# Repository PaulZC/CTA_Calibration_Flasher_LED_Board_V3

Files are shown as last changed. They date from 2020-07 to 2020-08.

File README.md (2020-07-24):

# CTA Calibration Flasher: LED Board V3

A nanosecond LED flasher board which provides digital control of both pulse width and LED current. Designed to aid
photomultiplier detector calibration and characterisation.

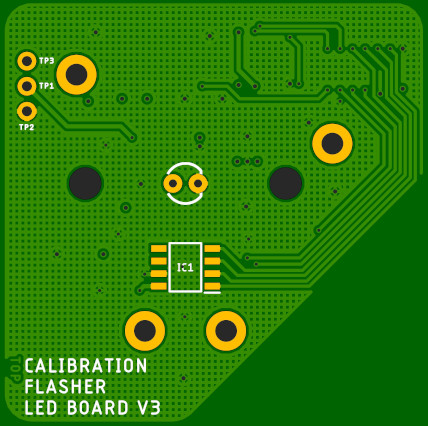
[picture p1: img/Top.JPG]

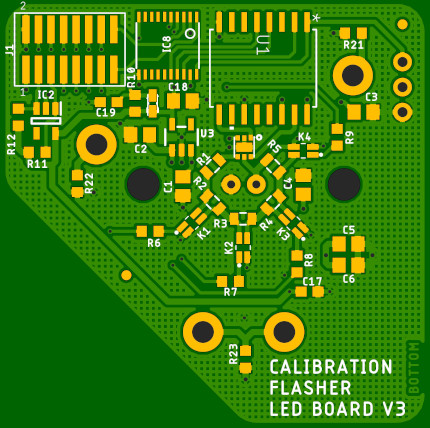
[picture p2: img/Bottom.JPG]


The design of this board is based extensively on that of the [Nanosecond LED Flasher Shield](https://github.com/PaulZC/Nanosecond_LED_Flasher_Shield).

The LED is driven by the [LMG1025 from Texas Instruments](http://www.ti.com/product/LMG1025-Q1).
Designed for automotive LIDAR applications, this gate driver has typical rise and fall times of 650ps
and 850ps and can produce 5V pulse widths as short as 1.25ns.

The pulse width is controlled by a [Maxim Integrated DS1023S-25+](https://www.maximintegrated.com/en/products/analog/clock-generation-distribution/DS1023.html)
programmable timing element which can produce digitally-adjustable pulse widths of 0 to ~64ns in 0.25ns increments.

The LED current is set by five surface mount resistors connected in series, four of which can be shorted
out by [Toshiba TLP3475 photorelays](https://toshiba.semicon-storage.com/ap-en/semiconductor/product/optoelectronics/photorelay-mosfet-output/detail.TLP3475.html)
allowing the LED current to be adjusted digitally in 16 increments.

The board is designed to be mounted on and controlled by the [CTA Calibration Flasher Controller Board V3](https://github.com/PaulZC/CTA_Calibration_Flasher_Controller_Board_V3).

The temperature can be measured via an [ADT7310 16-bit SPI temperature sensor](https://www.analog.com/en/products/adt7310.html).

The board is also equipped with a [DS28CM00 I<sup>2</sup>C silicon serial number](https://www.maximintegrated.com/en/products/ibutton-one-wire/memory-products/DS28CM00.html)
to allow the board to be uniquely identified during calibration.

To aid the mounting of a diffuser or fibre-coupling optics, a modified [ThorLabs S1LEDM SM1 threaded mount](https://www.thorlabs.de/thorproduct.cfm?partnumber=S1LEDM)
can be mounted onto the circuit board.

Please note that this board requires 5V power but that all I/O signals are 3.3V.

## Repository Contents

- **/Documentation** - Documentation for the hardware
- **/Hardware** - BOM, schematic, Eagle PCB design files and Gerber files
- **LICENSE.md** contains the licence information

## Documentation

- [Hardware overview](./Documentation/README.md): an overview of the hardware

Enjoy!

**_Paul_**

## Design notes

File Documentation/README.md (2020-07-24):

# CTA Calibration Flasher: LED Board V3: Hardware Overview

A nanosecond LED flasher board which provides digital control of both pulse width and LED current. Designed to aid
photomultiplier detector calibration and characterisation.

Top

Bottom

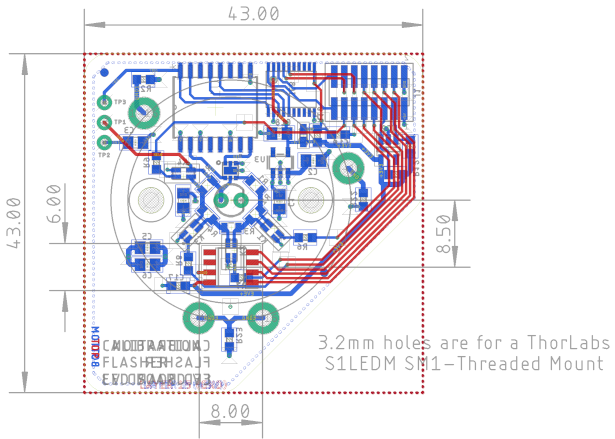
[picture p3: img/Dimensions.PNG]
Dimensions


The full schematic is available [here](../Hardware/Flasher_LED_Board_V3.pdf).

## LMG1025

The LED is driven by the new [LMG1025 from Texas Instruments](http://www.ti.com/product/LMG1025-Q1).
Designed for automotive LIDAR applications, this gate driver has typical rise and fall times of 650ps
and 850ps and can produce 5V pulse widths as short as 1.25ns.

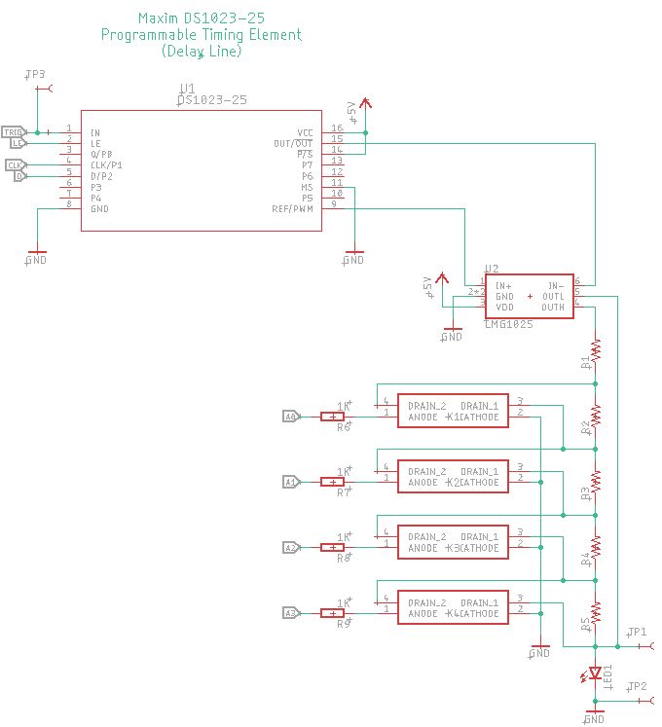
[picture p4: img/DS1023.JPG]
DS1023


The functional block diagram for the LMG1025 is:

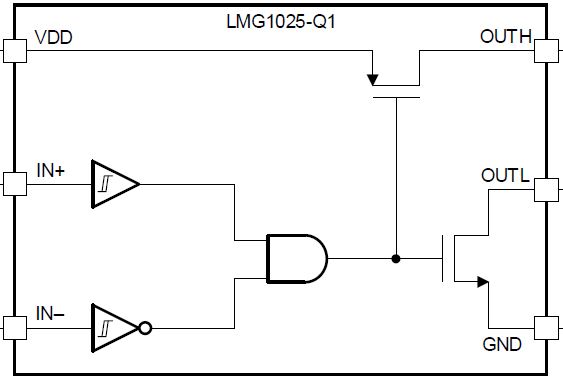
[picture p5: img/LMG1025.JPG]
LMG1025


The LMG1025 is designed to drive a GaN FET to switch a LIDAR source, but with pull-up and pull-down
current limits of 7A and 5A it can of course drive a standard or high-brightness LED directly.

The truth table for the LMG1025 is:

Truth Table

It is important to note that OUTH is pulled up to 5V only when IN+ is high and IN- is low. In each of the other
three possible states, OUTL is pulled low. We can take advantage of this by connecting OUTH to the current-limiting
resistor and OUTL directly to the LED anode. This allows the LED to be turned off very quickly.

## DS1023

The Maxim Integrated DS1023S-25+ is a programmable timing element with two outputs: OUT and REF. The delay between IN and
OUT is digitally-programmable from 0ns to ~64ns in 256 0.25ns increments. There is also an additional inherent "step zero"
delay between IN and OUT caused by the propagation delay through the chip. The REF output is delayed by a small fixed delay
of approximately 1.5ns plus the same "step zero" delay. By driving the LMG1025 IN+ and IN- from REF and OUT respectively,
the LED pulse can be adjusted from essentially zero pulse width (+/-0.125ns) to a maximum of 62.5ns (64ns - 1.5ns).
The LED turns on when REF goes high, and off again when OUT goes high.

## Photorelays

Five resistors, connected in series, are connected between the LMG1025 OUTH pin and the LED anode. By shorting out four
of these resistors in 16 permutations, the LED current can be adjusted between minimum and maximum values dictated by
the selection of resistor values. The resistors are shorted out by TLP3475 photorelays which provide fast response times
and an on-resistance of approximately 1ohm.

For example: with resistances of 10, 18, 22, 27 and 33 ohms, with the 10 ohm resistor always in circuit, it is possible to achieve
an even spread of resistance values from 13.8 ohms to 110 ohms.

## ADT7310

The temperature can be measured via an [ADT7310 16-bit SPI temperature sensor](https://www.analog.com/en/products/adt7310.html).

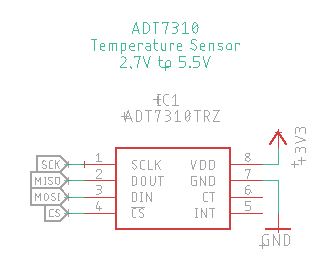
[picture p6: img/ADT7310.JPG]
ADT7310


## DS28CM00

The board is also equipped with a [DS28CM00 I<sup>2</sup>C silicon serial number](https://www.maximintegrated.com/en/products/ibutton-one-wire/memory-products/DS28CM00.html)
to allow the board to be uniquely identified during calibration.

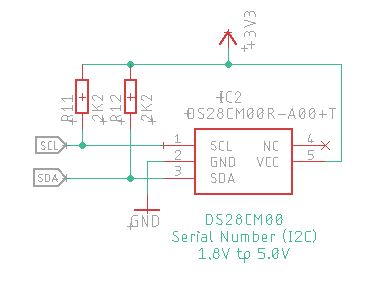
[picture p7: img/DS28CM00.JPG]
DS28CM00


## Connector

The connector is a [Samtec FW-08-05](https://www.samtec.com/products/fw-sm)

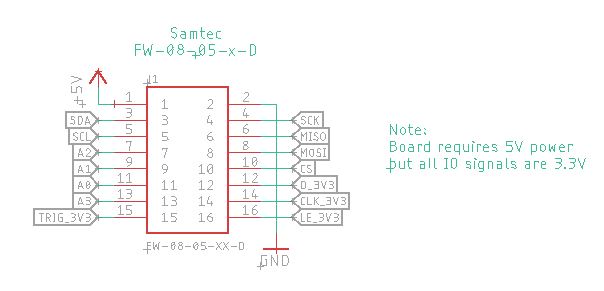
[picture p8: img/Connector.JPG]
Connector


The pin allocation is:
- 1: +5V power
- 2: GND (0V)
- 3: I<sup>2</sup>C SDA (DS28CM00)
- 4: SPI SCK (ADT7310)
- 5: I<sup>2</sup>C SCL (DS28CM00)
- 6: SPI CIPO (ADT7310)
- 7: Photorelay A2
- 8: SPI COPI (ADT7310)
- 9: Photorelay A1
- 10: SPI CS (ADT7310)
- 11: Photorelay A0
- 12: DS1023 Data
- 13: Photorelay A3
- 14: DS1023 CLK
- 15: Trigger signal
- 16: DS1023 Latch Enable

## TXB0108

To minimise congestion on the matching controller board, all I/O signals from the controller board to the LED board are 3.3V.
However, the DS1023 is of course a 5V device. A [TXB0108](https://www.ti.com/product/TXB0108) 8-bit bidirectional voltage-level shifter
converts the 3.3V signals to 5V.

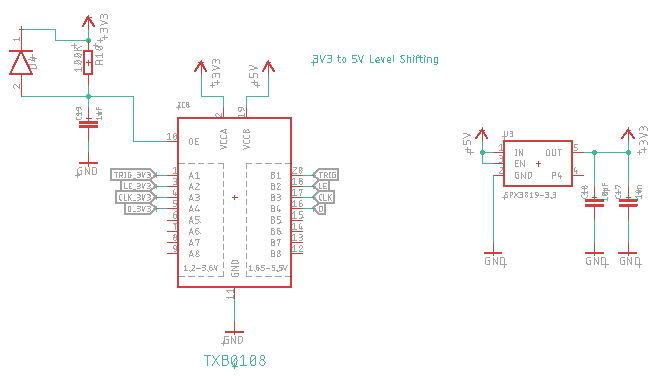
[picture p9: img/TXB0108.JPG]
TXB0108


## ThorLabs S1LEDM SM1

To aid the mounting of a diffuser or fibre-coupling optics, a modified [ThorLabs S1LEDM SM1 threaded mount](https://www.thorlabs.de/thorproduct.cfm?partnumber=S1LEDM)
can be mounted onto the circuit board.

It is necessary to:
- drill and tap the two spanner wrench slots to M3.0
  - the wrench slots are separated by 20.32mm in X
- mill a recess/pocket for the ADT7310
  - the pocket needs to be:
    - 8mm x 6mm
    - with a corner (tool) radius of 1mm
    - offset by 8.50mm in Y from the center of the part

Dimensions

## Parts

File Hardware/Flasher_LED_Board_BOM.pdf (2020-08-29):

Part | X | | Y | Angle | Package | Value | Manufacturer | Manufacturer Part No | Mouser Part No | Descripon
Dimensions 43.00 | 43.00

Fiducials - for solder paste mask alignment:

FD1 | 2.54 | 40.46 | 40.64 | 0 | | | | | | Fiducial 1mm
FD2 | 30.48 | 12.52 | 15.24 | 0 | | | | | | Fiducial 1mm

Surface Mount Components (Top):

IC1 | 18.62 | 16.94 | 180 | 8-Lead SOIC_N (R-8) ADT7310TRZ | Analog Devices | ADT7310TRZ | 2067805 584-ADT7310TRZ-R7 | Temperature Sensor IC, Digital, ± 0.5°C, -55 °C, +150 °C

Surface Mount Components (Boom):

C1 | 24.77 | 18.23 | 24.26 | 270 | 0805 | 10nF | Walsin | 0805B103K500CT | 2496939 | MulLayer Ceramic Capacitor; 10nF; 50V; 0805; X7R
C2 | 29.08 | 13.92 | 29.46 | 180 | 0805 | 10uF | Walsin | 0805F106Z100CT | 2496998 | MulLayer Ceramic Capacitor; 10uF; 10V; 0805
C3 | 6.48 | 36.52 | 31.75 | 0 | 0805 | 10nF | Walsin | 0805B103K500CT | 2496939 | MulLayer Ceramic Capacitor; 10nF; 50V; 0805; X7R
C4 | 12.57 | 30.43 | 24.38 | 90 | 0805 | 10uF | Walsin | 0805F106Z100CT | 2496998 | MulLayer Ceramic Capacitor; 10uF; 10V; 0805
C5 | 8 | 35.00 | 18.41 | 0 | 0805 | 10nF | Walsin | 0805B103K500CT | 2496939 | MulLayer Ceramic Capacitor; 10nF; 50V; 0805; X7R
C6 | 8 | 35.00 | 16.26 | 0 | 0805 | 10uF | Walsin | 0805F106Z100CT | 2496998 | MulLayer Ceramic Capacitor; 10uF; 10V; 0805
C17 | 11.94 | 31.06 | 13.59 | 0 | 0603 | 10nF | Walsin | 0201B103K100CT | 2496756 | MulLayer Ceramic Capacitor; 10nF; 10V; 0603; X7R
C18 | 24.77 | 18.23 | 32.89 | 0 | 0805 | 10uF | Walsin | 0805F106Z100CT | 2496998 | MulLayer Ceramic Capacitor; 10uF; 10V; 0805
C19 | 32.26 | 10.74 | 32.77 | 180 | 0603 | 1uF | Walsin | 0603X105K100CT | 2496916 | MulLayer Ceramic Capacitor; 1uF; 10V; 0603; X5R
D4 | 27.81 | 15.19 | 32.64 | 90 | 0603 | CD0603-B00340 | Bourns | CD0603-B00340 | 1456534 | Small Signal Schoky Diode, 40 V, 370 mV, 500 mA
IC2 | 38.61 | 4.39 | 30.86 | 270 | SOT23-5 | DS28CM00R-A00+T | Maxim | DS28CM00R-A00+T | 2514574 700-DS28CM00R-A00T | Maxim (Dallas Semi) I2C/SMBus Silicon Serial Number
IC8 | 26.29 | 16.71 | 38.48 | 180 | TSSOP20 | TXB0108PWR | Texas Inst. | TXB0108PWR | 1494945 | Voltage Level Translator; 8 Input; TSSOP-20
J1 | 36.2 | 6.80 | 38.1 | 0 | | | Samtec
K1 | 23.85 | 19.15 | 20.55 | 315 | | | Toshiba | TLP3475RTPF | 757-TLP3475TPF | Toshiba TLP3475 Photorelay (not TLP3475R)
K2 | 18.65 | 24.35 | 18.03 | 0 | | | Toshiba | TLP3475RTPF | 757-TLP3475TPF | Toshiba TLP3475 Photorelay (not TLP3475R)
K3 | 13.56 | 29.44 | 20.48 | 45 | | | Toshiba | TLP3475RTPF | 757-TLP3475TPF | Toshiba TLP3475 Photorelay (not TLP3475R)
K4 | 12.57 | 30.43 | 27.83 | 90 | | | Toshiba | TLP3475RTPF | 757-TLP3475TPF | Toshiba TLP3475 Photorelay (not TLP3475R)
R1 | 21.72 | 21.28 | 26.29 | 45 | 0805 | | | | | Select on test: suggested value 10R
R2 | 21.72 | 21.28 | 22.61 | 135 | 0805 | | | | | Select on test: suggested value 18R
R3 | 18.67 | 24.33 | 20.96 | 180 | 0805 | | | | | Select on test: suggested value 22R
R4 | 15.62 | 27.38 | 22.61 | 225 | 0805 | | | | | Select on test: suggested value 27R
R5 | 15.62 | 27.38 | 26.29 | 315 | 0805 | | | | | Select on test: suggested value 33R
R6 | 28.07 | 14.93 | 19.69 | 180 | 0603 | 1K | Mulcomp | MCWR06X1001FTL | 2447272 | Chip Resistor; Thick Film; 1k; 50V; 0603; 100mW
R7 | 19.94 | 23.06 | 14.61 | 180 | 0603 | 1K | Mulcomp | MCWR06X1001FTL | 2447272 | Chip Resistor; Thick Film; 1k; 50V; 0603; 100mW
R8 | 13.21 | 29.79 | 16.38 | 270 | 0603 | 1K | Mulcomp | MCWR06X1001FTL | 2447272 | Chip Resistor; Thick Film; 1k; 50V; 0603; 100mW
R9 | 9.14 | 33.86 | 29.21 | 90 | 0603 | 1K | Mulcomp | MCWR06X1001FTL | 2447272 | Chip Resistor; Thick Film; 1k; 50V; 0603; 100mW
R10 | 29.59 | 13.41 | 32.64 | 90 | 0603 | 100K | Mulcomp | MCWR06X1002FTL | 2447230 | Chip Resistor; Thick Film; 10k; 50V; 0603; 100mW
R11 | 39.5 | 3.50 | 27.69 | 180 | 0603 | 2K2 | Mulcomp | MCWR06X2201FTL | 2447320 | Chip Resistor; Thick Film; 2.2k; 50V; 0603; 100mW
R12 | 41.4 | 1.60 | 31.24 | 270 | 0603 | 2K2 | Mulcomp | MCWR06X2201FTL | 2447320 | Chip Resistor; Thick Film; 2.2k; 50V; 0603; 100mW
R21 | 7.49 | 35.51 | 39.75 | 180 | 0603 | 0R | Mulcomp | MCMR06X000PTL | 2073345 | SMD Chip Resistor, 0 ohm, 75 V, 0603, 100 mW
R22 | 35.43 | 7.57 | 24.51 | 270 | 0603 | 0R | Mulcomp | MCMR06X000PTL | 2073345 | SMD Chip Resistor, 0 ohm, 75 V, 0603, 100 mW
R23 | 18.41 | 24.59 | 6.73 | 270 | 0603 | 0R | Mulcomp | MCMR06X000PTL | 2073345 | SMD Chip Resistor, 0 ohm, 75 V, 0603, 100 mW
U1 | 16.64 | 26.36 | 36.2 | 270 | WSOIC-16 | DS1023-25 | Maxim | DS1023S-25+ | 2516605 700-DS1023S-25 | Delay Line; 256 taps; 250ps delay/tap; WSOIC-16
U2 | 18.54 | 24.46 | 28.19 | 180 | LMG1025 | LMG1025
U3 | 24.89 | 18.11 | 29.21 | 0 | SOT23-5 | SPX3819-3.3 | Exar | SPX3819M5-L-3-3/TR | 701-SPX3819M5-L-33TR | LDO Voltage Regulator; 500mA; SOT-23-5

Non-surface mount components:

LED | | | | | | | Bivar | UV3TZ-400-15 | | Ultraviolet LED, 3mm, 10mW, 400nm, 15 deg, 3.3V, 20mA Max, RS Part: 713-5021P

X
(Mirrored)

Angle
(Mirrored)

Farnell
Part No

TI LMG1025: https://www.ti.com/product/LMG1025-Q1

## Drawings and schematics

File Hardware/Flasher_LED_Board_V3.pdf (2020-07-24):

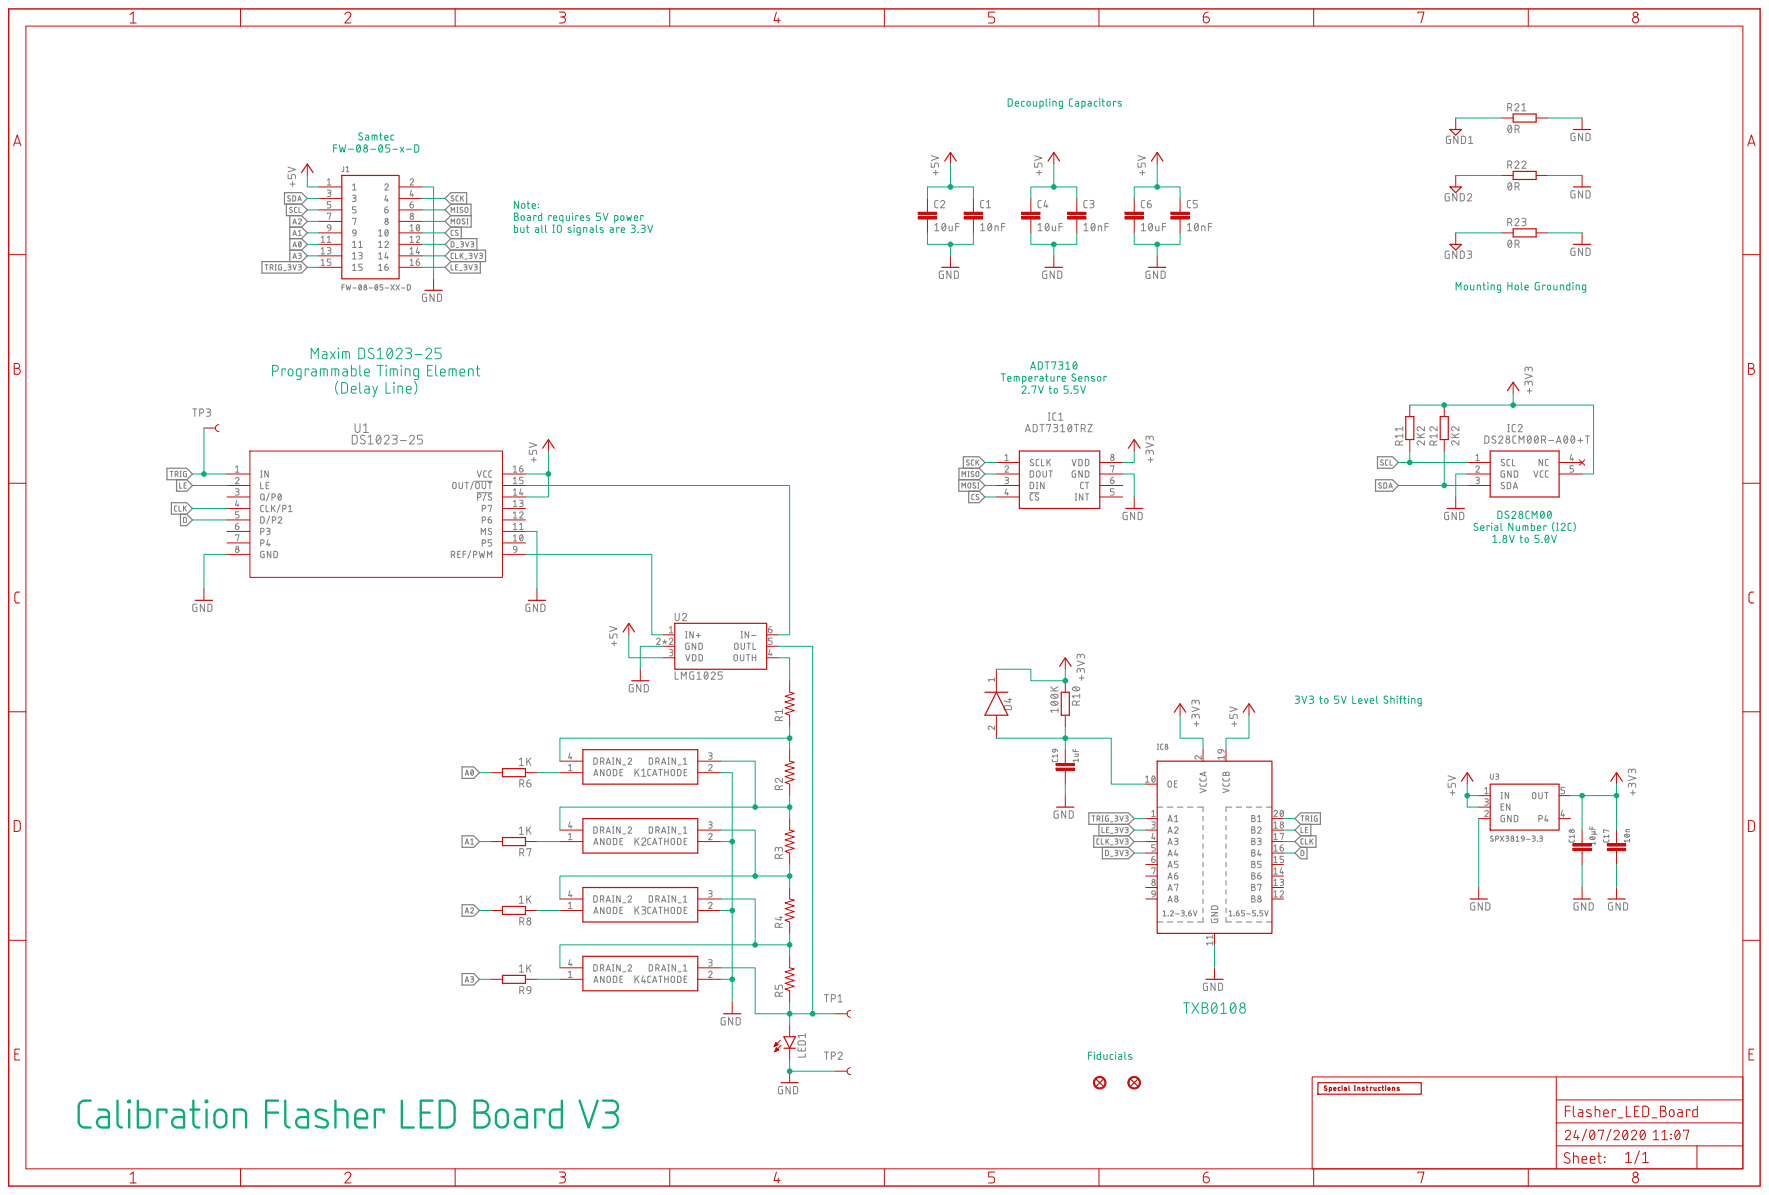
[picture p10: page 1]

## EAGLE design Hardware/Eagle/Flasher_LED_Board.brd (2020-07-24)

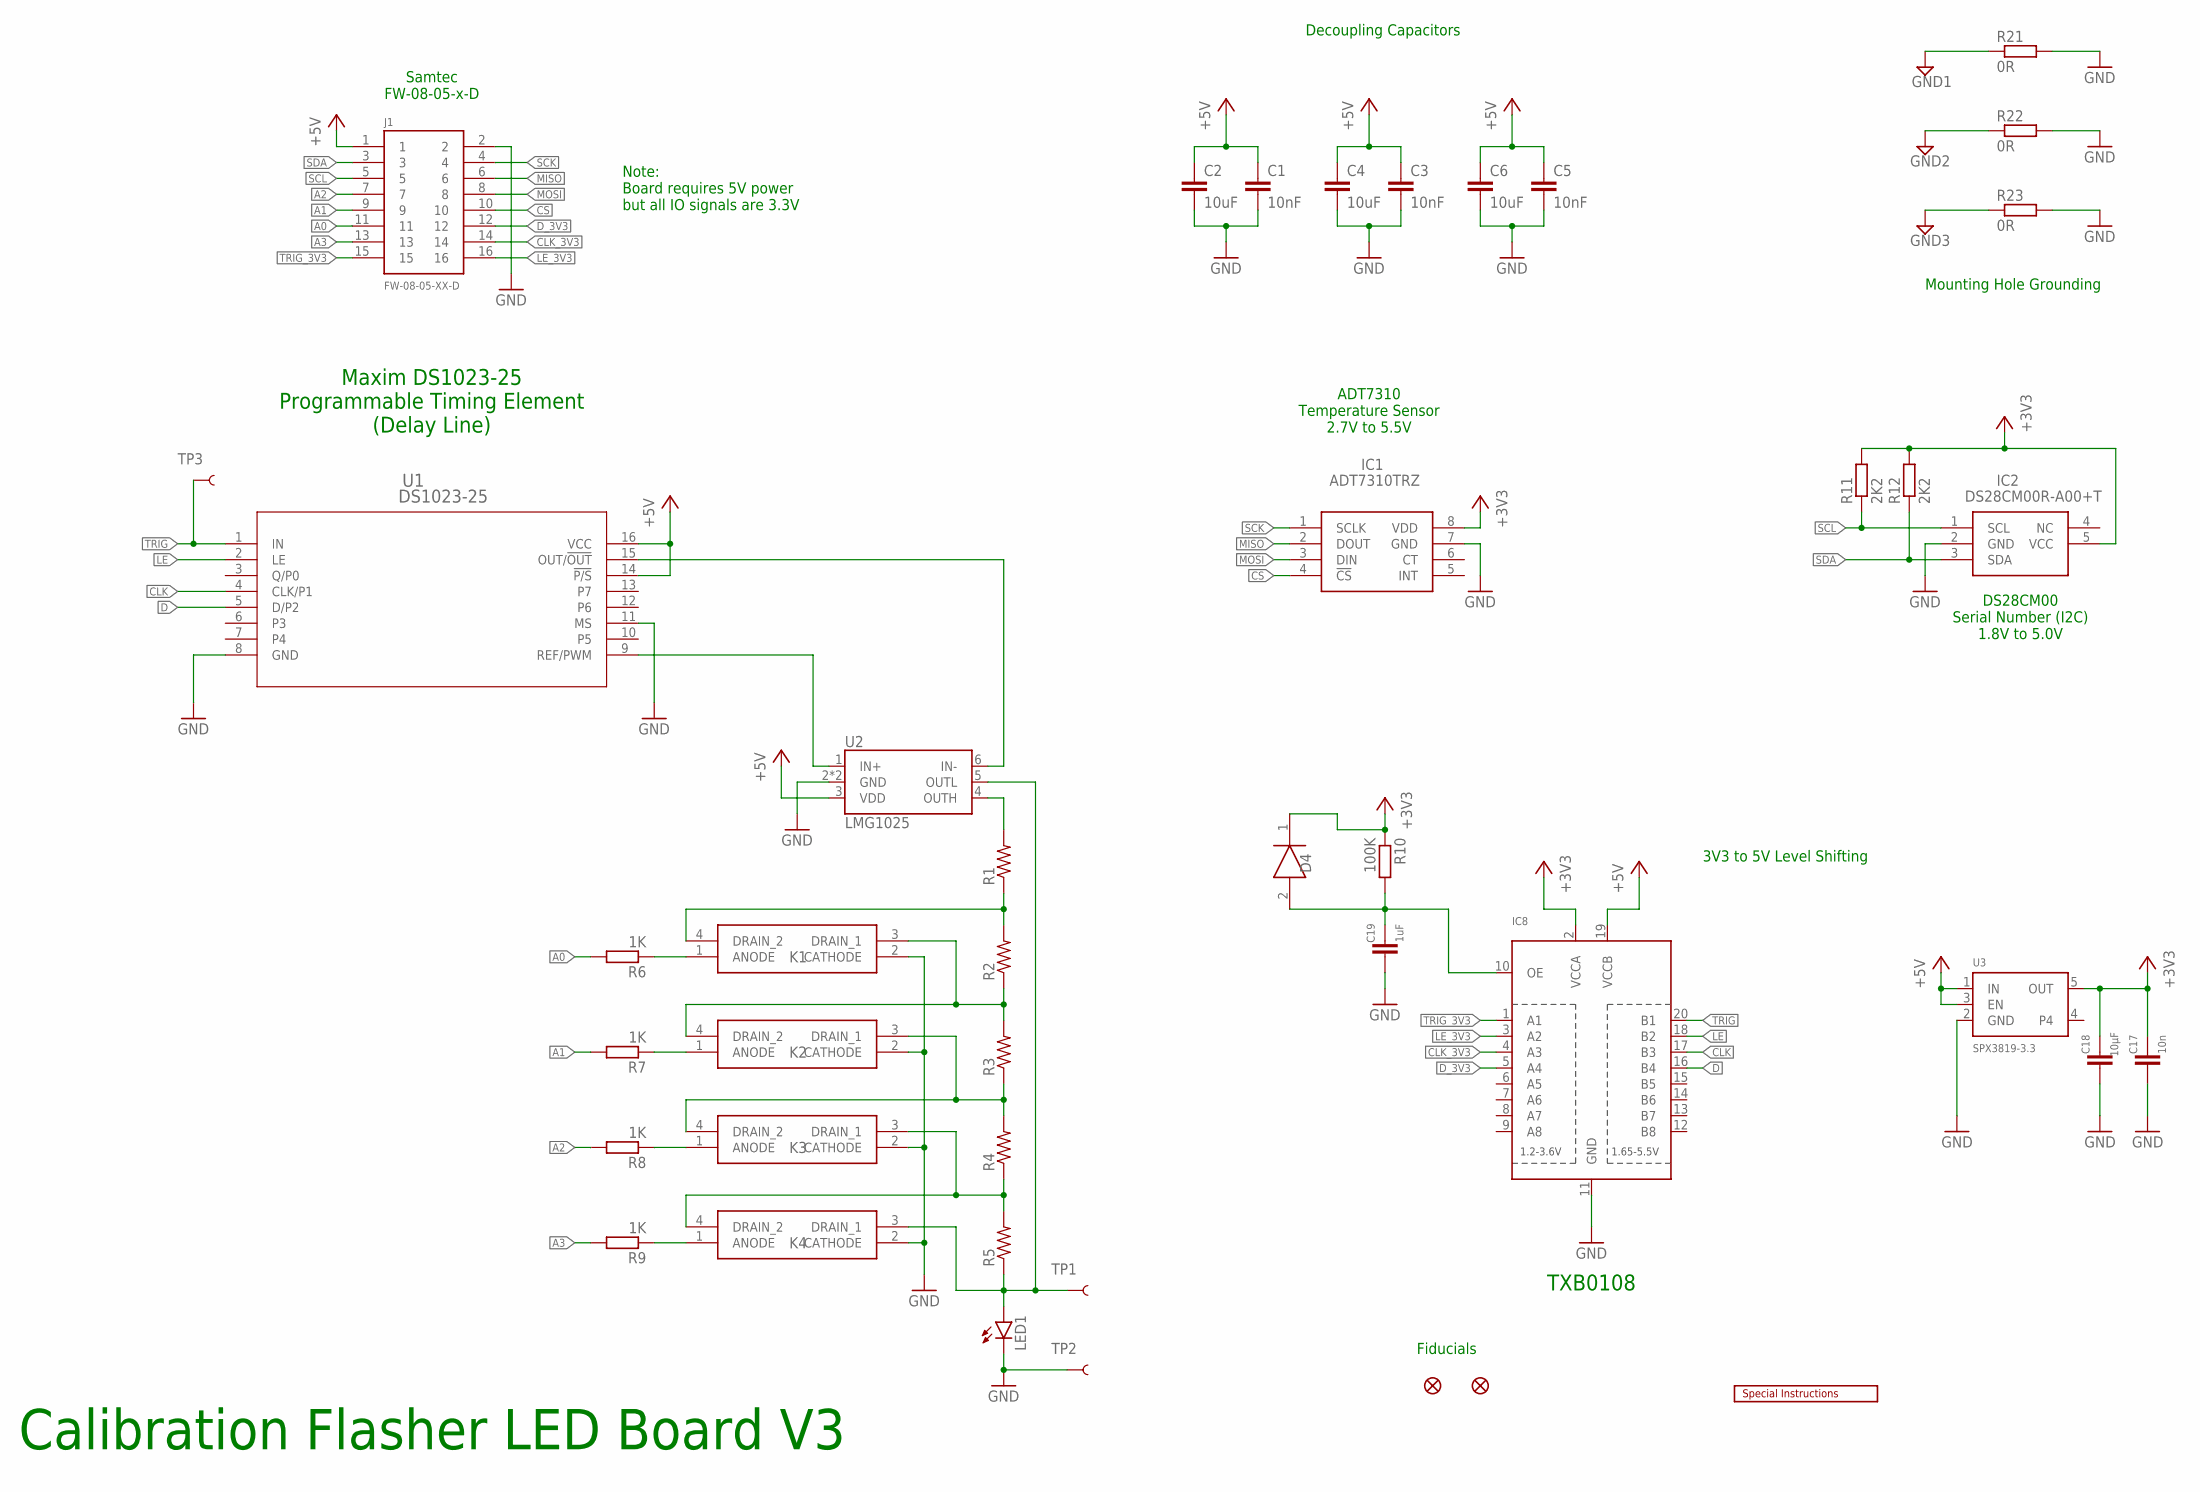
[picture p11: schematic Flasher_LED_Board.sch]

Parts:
C1, C3, C5: 10nF; C0805
C2, C4, C6: 10uF; C0805
C17: 10n; C0603
C18: 10µF; C0805
C19: 1uF; C0603
D4: CD0603-B00340; DIOM179X85N
FD1, FD2: FIDUCIAL1X2; FIDUCIAL-1X2
IC1: ADT7310TRZ; SOIC127P600X175-8N
IC2: DS28CM00R-A00+T; SOT95P280X145-5N
IC8: TXB0108PWR; TSSOP20
J1: FW-08-05-XX-D
K1, K2, K3, K4: TLP3475R(TP,F; TLP3475RTPF
LED1: LED3MM
LOGO6: SPECIAL_INSTRUCTIONS-ORDERING; ORDERING_INSTRUCTIONS
R1, R2, R3, R4, R5: RESISTOR0805-RES; 0805
R6, R7, R8, R9: 1K; R0603
R10: 100K; R0603
R11, R12: 2K2; R0603
R21, R22, R23: 0R; R0603
TP1, TP2, TP3: TEST-POINTPOGO_PTH; 1X01_NO_SILK
U1: DS1023-25; 21-0042B_16
U2: LMG1025
U3: SPX3819-3.3; SOT23-5

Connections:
+3V3: C17.1, C18.1, D4.1 (K), IC1.8 (VDD), IC2.5 (VCC), IC8.2 (VCCA), R10.1, R11.2, R12.2, U3.5 (OUT)
+5V: C1.1, C2.1, C3.1, C4.1, C5.1, C6.1, IC8.19 (VCCB), J1.1, U1.14 (!P/S), U1.16 (VCC), U2.3 (VDD), U3.1 (IN), U3.3 (EN)
A0: J1.11, R6.2
A1: J1.9, R7.2
A2: J1.7, R8.2
A3: J1.13, R9.2
CLK: IC8.17 (B3), U1.4 (CLK/P1)
CLK_3V3: IC8.4 (A3), J1.14
CS: IC1.4 (!CS), J1.10
D: IC8.16 (B4), U1.5 (D/P2)
D_3V3: IC8.5 (A4), J1.12
GND: C1.2, C2.2, C3.2, C4.2, C5.2, C6.2, C17.2, C18.2, C19.2, IC1.7 (GND), IC2.2 (GND), IC8.11 (GND), J1.2, K1.2 (CATHODE), K2.2 (CATHODE), K3.2 (CATHODE), K4.2 (CATHODE), LED1.K (C), R21.2, R22.2, R23.2, TP2.1, U1.8 (GND), U1.11 (MS), U2.2 (GND), U2.PAD (GND), U3.2 (GND)
GND1: R21.1
GND2: R22.1
GND3: R23.1
LE: IC8.18 (B2), U1.2 (LE)
LE_3V3: IC8.3 (A2), J1.16
MISO: IC1.2 (DOUT), J1.6
MOSI: IC1.3 (DIN), J1.8
unnamed: C19.1, D4.2 (A), IC8.10 (OE), R10.2
unnamed: U1.15 (OUT/!OUT), U2.6 (IN-)
unnamed: U1.9 (REF/PWM), U2.1 (IN+)
unnamed: R1.2, U2.4 (OUTH)
unnamed: K1.4 (DRAIN_2), R1.1, R2.2
unnamed: K1.3 (DRAIN_1), K2.4 (DRAIN_2), R2.1, R3.2
unnamed: K2.3 (DRAIN_1), K3.4 (DRAIN_2), R3.1, R4.2
unnamed: K3.3 (DRAIN_1), K4.4 (DRAIN_2), R4.1, R5.2
unnamed: K4.3 (DRAIN_1), LED1.A, R5.1, TP1.1, U2.5 (OUTL)
unnamed: K1.1 (ANODE), R6.1
unnamed: K2.1 (ANODE), R7.1
unnamed: K3.1 (ANODE), R8.1
unnamed: K4.1 (ANODE), R9.1
SCK: IC1.1 (SCLK), J1.4
SCL: IC2.1 (SCL), J1.5, R11.1
SDA: IC2.3 (SDA), J1.3, R12.1
TRIG: IC8.20 (B1), TP3.1, U1.1 (IN)
TRIG_3V3: IC8.1 (A1), J1.15

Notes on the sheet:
Calibration Flasher LED Board V3
Samtec FW-08-05-x-D
Fiducials
Mounting Hole Grounding
Decoupling Capacitors
Maxim DS1023-25 Programmable Timing Element (Delay Line)
ADT7310 Temperature Sensor 2.7V to 5.5V
DS28CM00 Serial Number (I2C) 1.8V to 5.0V
TXB0108
3V3 to 5V Level Shifting
Note: Board requires 5V power but all IO signals are 3.3V

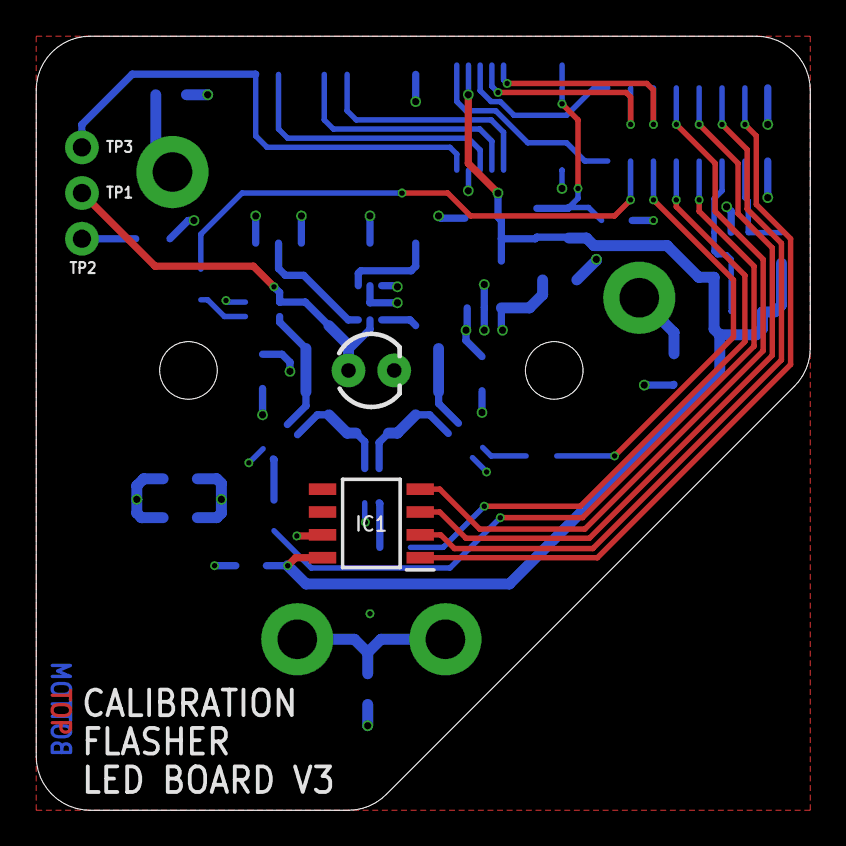
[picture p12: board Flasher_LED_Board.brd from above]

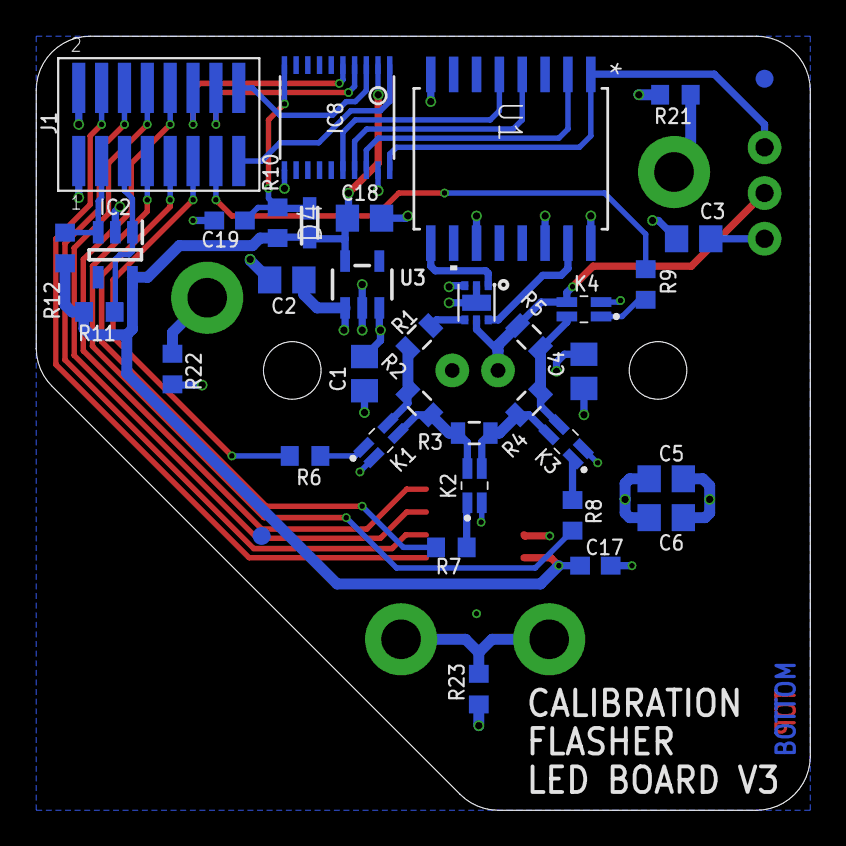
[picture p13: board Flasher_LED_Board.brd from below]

Board: 4 copper layers, 43.0 x 43.0 mm, 43 parts (37 on the bottom side), 34 nets.

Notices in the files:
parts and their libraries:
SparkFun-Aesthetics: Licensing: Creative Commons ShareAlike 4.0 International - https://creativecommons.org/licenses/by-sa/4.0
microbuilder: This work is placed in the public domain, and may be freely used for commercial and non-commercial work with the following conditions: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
